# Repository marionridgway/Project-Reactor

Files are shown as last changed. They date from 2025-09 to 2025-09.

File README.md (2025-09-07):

# Project-Reactor
Smart 3D Printed UV Flow Reactor Monitoring and Control System. A digitally-controlled reactor using Arduino Uno R4 WiFi, Node-RED Dashboard, and Python for real-time monitoring, sensor logging (temperature, turbidity, UV, RGB), and  actuator control. Includes data logging to SQLite and serial integration with a customisable dashboard.

# Project Objectives

- Real-time visualisation of temperature, UV intensity, turbidity, and RGB sensor data
- Digital control of UV LEDs and peristaltic pumps
- Track and analyse dye degradation behavior
- Store all experimental data for post-run analysis using SQLite
- Sense and response of reactor parameters

# System Architecture

- Arduino UNO R4 WiFi
↓ Serial USB
- Node-Red Dashboard
↓ TCP socket (localhost)
- Python Script -> SQLite Database

# Technologies Used

- Arduino Uno R4 WiFi — Microcontroller with built-in ESP32 co-processor
- Node-RED — Dashboard and serial communication
- Python 3 — Data logger and tools
- SQLite — Local file-based database for experimental data
- Temperature Sensor: LM35 
- UV Sensor: GUVA-S12SD
- Turbidity: SKU SEN0189 
- Colour: TCS3200 
- Phototransistor: SFH 3310 
- LEDs: Blue: HLMP-AB64-TW0xx 
- LEDs UV: VAOL-5GUV8T4 
- Pumps: SKU DFR0523 

reactor-project/
├── arduino_firmware/ # Arduino .ino files and libraries
├── python_logging/ # Python scripts for logging to SQLite
├── node_red/ # Exported Node-RED flows (.json)
├── database/ # Python to SQLite .db file
├── media/ # Screenshots, wiring diagrams
└── README.md # This file

# How to Run

----> 1. Upload Arduino Firmware
- Open `arduino_firmware/` in the Arduino IDE
- Select board: `Arduino Uno R4 WiFi`
- Upload the sketch to your board

----> 2. Start Node-RED
- Control using dashboard at localhost

----> 3. Run Python Logger
- Saves data to SQLite

----> 4. Open Database (optional)
- Observe Data

# Authors

Marion Ridgway
MSc Researcher

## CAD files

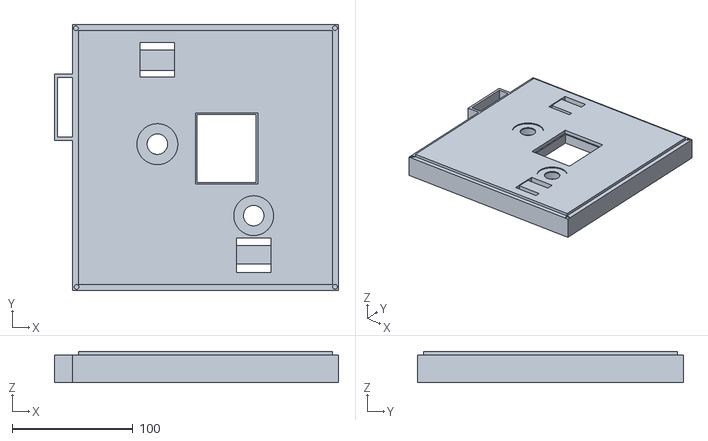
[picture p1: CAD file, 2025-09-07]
Plate_B_Sense.stl
235.0 x 220.0 x 26.0

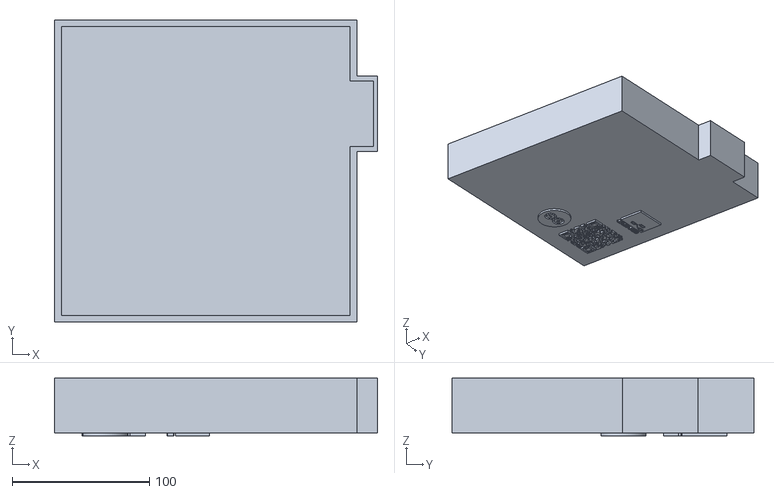
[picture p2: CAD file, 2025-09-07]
Plate_A_Top.stl
235.0 x 220.0 x 42.0

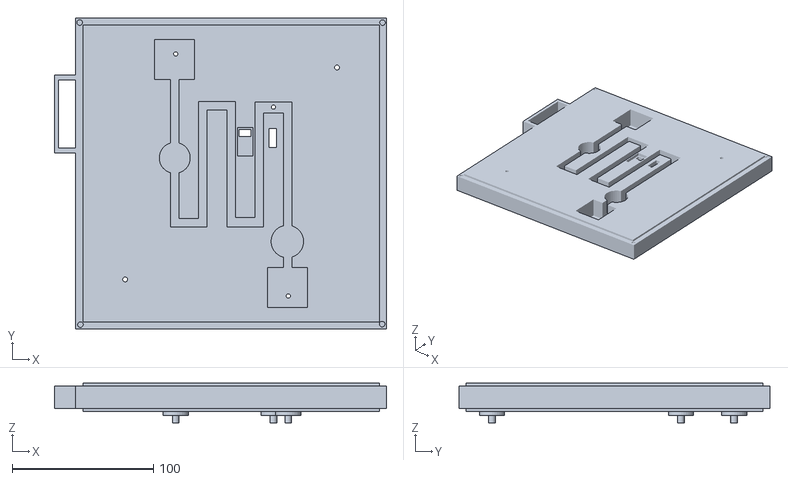
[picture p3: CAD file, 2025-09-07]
Plate_C_Flow.stl
235.0 x 220.0 x 28.0

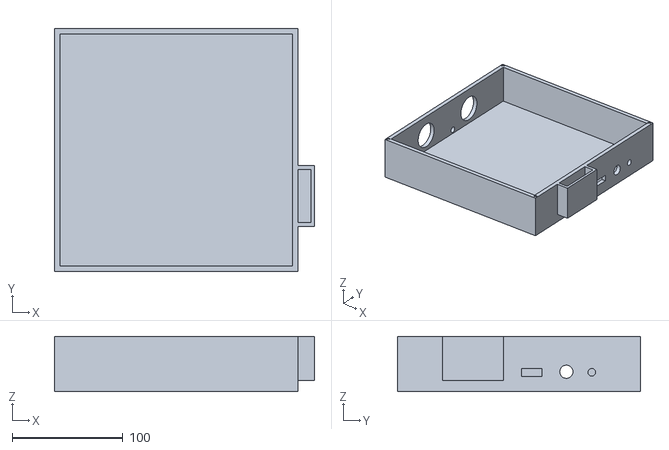
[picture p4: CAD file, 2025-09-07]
Plate_D_Base.stl
235.0 x 220.0 x 50.0

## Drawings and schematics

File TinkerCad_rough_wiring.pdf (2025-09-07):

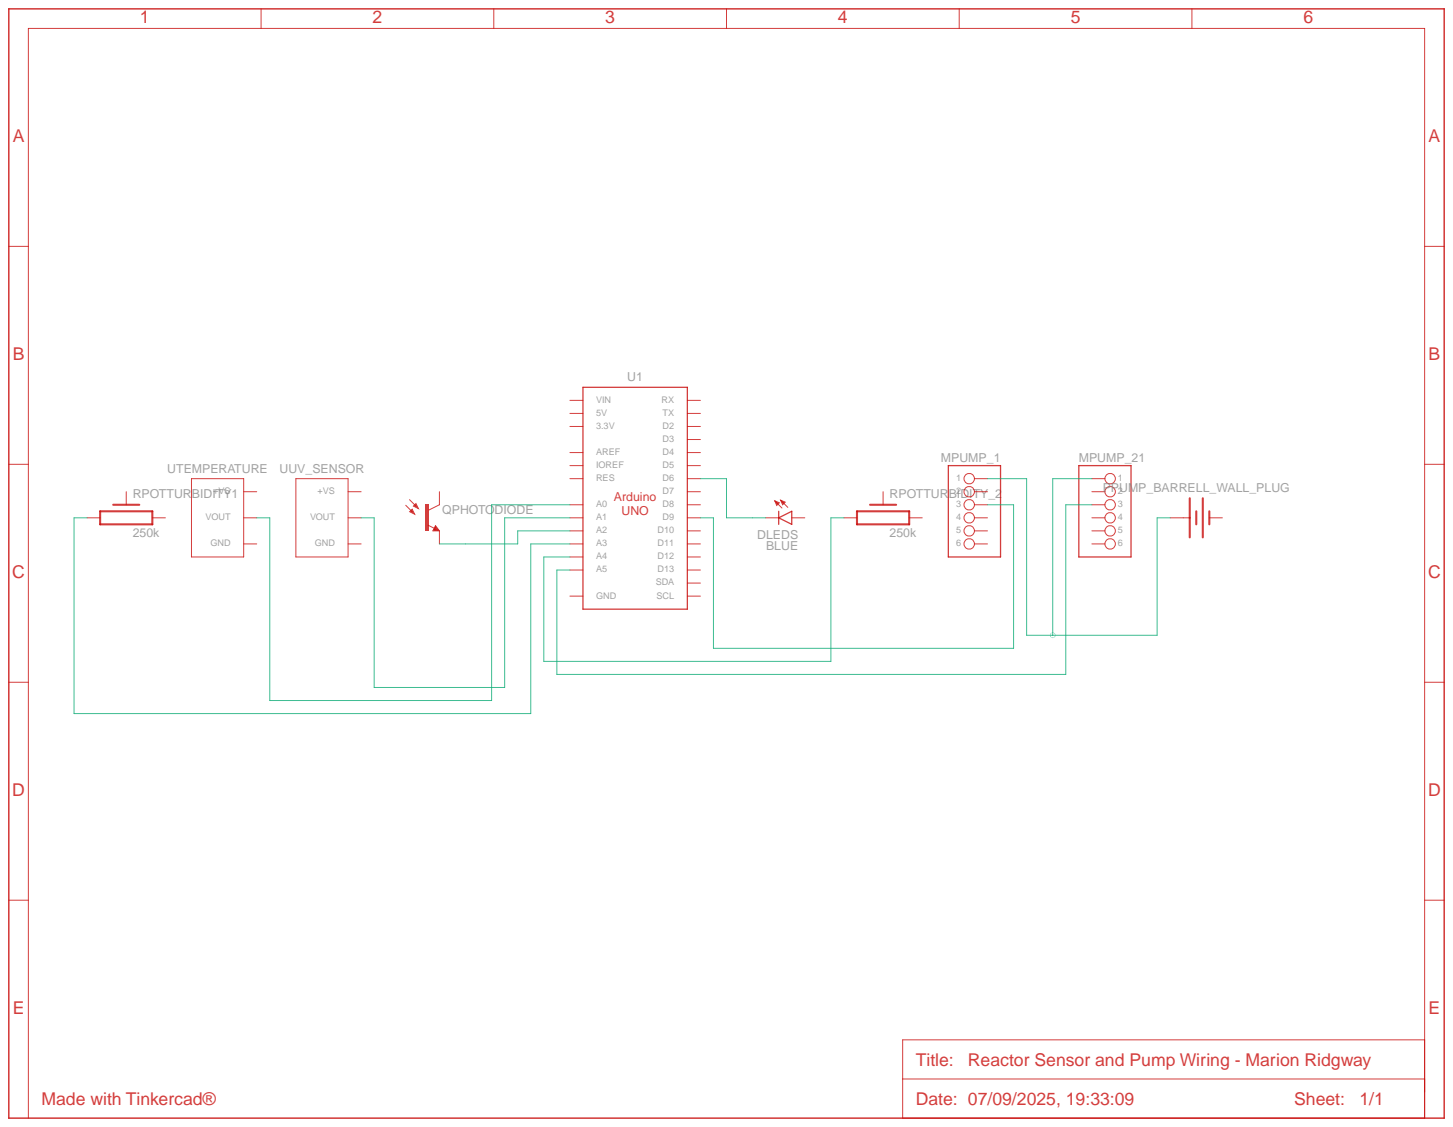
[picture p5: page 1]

Title: Reactor Sensor and Pump Wiring - Marion Ridgway

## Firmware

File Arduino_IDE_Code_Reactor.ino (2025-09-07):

/*
  Reactor Sensor Hub (Arduino)
  ---------------------------
  - Reads two TCS3200 color sensors (RGB1, RGB2)
  - RGB1 uses a fixed "Preset 1" mapping that matched wiring:
      RED=HL, GREEN=HH, BLUE=LH, CLEAR=LL  (S2/S3)
  - Reads temperature (A0), UV sensor (A1), photodiode (A2), turbidity2 (A4)
    (turbidity1 was removed; JSON keeps the key with 0.00 to avoid breaking Node-RED)
  - Drives Pump 1 (DC via GravityPump on D9) and Pump 2 (servo on A5)
  - Streams a single JSON object per loop for Node-RED

  Serial commands
  ---------------
  - "led on at intensity:<0..255>"   e.g. "led on at intensity:128"
  - "led off"
  - "pump:<mL>"                      e.g. "pump: 1.5"
  - "pump:<mL> at speed:<0..89>"     e.g. "pump: 1.5 at speed:30"
  - "pump2:<mL>"                     e.g. "pump2: 0.250"
  - "pump stop" / "pump2 stop"

  Notes
  -----
  - Keep white illumination on the sample for meaningful color readings.
  - A3 must be interrupt-capable on board for RGB1 OUT. 
*/

#include <Servo.h>
#include "GravityPump.h"
#include <EEPROM.h>
#include <math.h>

enum TCSChan { TCS_RED, TCS_GREEN, TCS_BLUE, TCS_CLEAR };

const int tempSensorPin = A0;
const int uvSensor1Pin  = A1;
const int photodiodePin = A2;
const int turbidityPin2 = A4;

const int uvLedPin1 = 6;
const int pumpPin   = 9;
const int pump2Pin  = A5;

const int s0_1 = 4, s1_1 = 5, s2_1 = 3, s3_1 = 7;
const int out_1 = A3;
const int s0_2 = 8, s1_2 = 10, s2_2 = 11, s3_2 = 12;
const int out_2 = 2;

const float alpha = 0.3f;
const unsigned GATE_MS = 100;
float vcc = 4.63;

const float pump2FlowRate   = 0.01f;
const int   pump2SpeedAngle = 10;

Servo pump2Servo;
GravityPump pump;

bool uvState = false;
bool pumpState = false;
bool pump2State = false;
int  uvLedIntensity = 0;

unsigned long pumpEndTime  = 0;
unsigned long pump2EndTime = 0;
int lastPumpSpeed = 0;

static String lastPump1Command = "";

volatile uint32_t counter1 = 0, counter2 = 0;
float r1=0,g1=0,b1=0,c1=0;
float r2=0,g2=0,b2=0,c2=0;

static inline uint8_t gamma22(float v) {
  if (v < 0) v = 0;
  if (v > 1) v = 1;
  return (uint8_t)(255.0 * pow(v, 1.0/2.2));
}

int readSmoothedAnalog(int pin, int samples = 20) {
  analogRead(pin);
  delayMicroseconds(200);
  long total = 0;
  for (int i = 0; i < samples; i++) { total += analogRead(pin); delay(2); }
  return total / samples;
}

float getCalibratedFlowRate() {
  float value;
  byte *ptr = (byte*)&value;
  for (int i = 0; i < (int)sizeof(value); i++) ptr[i] = EEPROM.read(0x24 + i);
  return value;
}

void ISR_sensor1() { counter1++; }
void ISR_sensor2() { counter2++; }

void tcsSelect(int s2, int s3, TCSChan c) {
  switch (c) {
    case TCS_RED:   digitalWrite(s2, LOW);  digitalWrite(s3, LOW);  break;
    case TCS_GREEN: digitalWrite(s2, HIGH); digitalWrite(s3, HIGH); break;
    case TCS_BLUE:  digitalWrite(s2, LOW);  digitalWrite(s3, HIGH); break;
    case TCS_CLEAR: digitalWrite(s2, HIGH); digitalWrite(s3, LOW);  break;
  }
}

uint32_t tcsReadCounts(volatile uint32_t &ctr, unsigned gate_ms) {
  noInterrupts(); ctr = 0; interrupts();
  uint32_t t0 = millis();
  while (millis() - t0 < gate_ms) {}
  noInterrupts(); uint32_t counts = ctr; interrupts();
  return counts;
}

void readTCS3200(int s2, int s3, volatile uint32_t &ctr, float &R, float &G, float &B, float &C) {
  uint32_t rC, gC, bC, cC;
  tcsSelect(s2, s3, TCS_RED);   rC = tcsReadCounts(ctr, GATE_MS);
  tcsSelect(s2, s3, TCS_GREEN); gC = tcsReadCounts(ctr, GATE_MS);
  tcsSelect(s2, s3, TCS_BLUE);  bC = tcsReadCounts(ctr, GATE_MS);
  tcsSelect(s2, s3, TCS_CLEAR); cC = tcsReadCounts(ctr, GATE_MS);
  R = alpha * (float)rC + (1 - alpha) * R;
  G = alpha * (float)gC + (1 - alpha) * G;
  B = alpha * (float)bC + (1 - alpha) * B;
  C = alpha * (float)cC + (1 - alpha) * C;
}

void readTCS3200_rgb1_fixed(int s2, int s3, volatile uint32_t &ctr, float &R, float &G, float &B, float &C) {
  uint32_t rC, gC, bC, cC;
  digitalWrite(s2, HIGH); digitalWrite(s3, LOW);   rC = tcsReadCounts(ctr, GATE_MS);
  digitalWrite(s2, HIGH); digitalWrite(s3, HIGH);  gC = tcsReadCounts(ctr, GATE_MS);
  digitalWrite(s2, LOW);  digitalWrite(s3, HIGH);  bC = tcsReadCounts(ctr, GATE_MS);
  digitalWrite(s2, LOW);  digitalWrite(s3, LOW);   cC = tcsReadCounts(ctr, GATE_MS);
  R = alpha * (float)rC + (1 - alpha) * R;
  G = alpha * (float)gC + (1 - alpha) * G;
  B = alpha * (float)bC + (1 - alpha) * B;
  C = alpha * (float)cC + (1 - alpha) * C;
}

void setup() {
  Serial.begin(9600);

  pinMode(tempSensorPin, INPUT);
  pinMode(uvSensor1Pin, INPUT);
  pinMode(photodiodePin, INPUT);
  pinMode(turbidityPin2, INPUT);
  pinMode(uvLedPin1, OUTPUT);

  pinMode(s0_1, OUTPUT); pinMode(s1_1, OUTPUT); pinMode(s2_1, OUTPUT); pinMode(s3_1, OUTPUT);
  pinMode(out_1, INPUT);
  pinMode(s0_2, OUTPUT); pinMode(s1_2, OUTPUT); pinMode(s2_2, OUTPUT); pinMode(s3_2, OUTPUT);
  pinMode(out_2, INPUT);

  digitalWrite(s0_1, HIGH); digitalWrite(s1_1, LOW);
  digitalWrite(s0_2, HIGH); digitalWrite(s1_2, LOW);

  attachInterrupt(digitalPinToInterrupt(out_1), ISR_sensor1, FALLING);
  attachInterrupt(digitalPinToInterrupt(out_2), ISR_sensor2, FALLING);

  pump.setPin(pumpPin);
  pump.getFlowRateAndSpeed();
}

void loop() {
  readTCS3200_rgb1_fixed(s2_1, s3_1, counter1, r1, g1, b1, c1);
  readTCS3200(s2_2, s3_2, counter2, r2, g2, b2, c2);

  pump.update();
  if (pumpState && millis() > pumpEndTime) pumpState = false;
  if (pump2State && millis() > pump2EndTime) {
    pump2Servo.write(90); pump2Servo.detach(); pump2State = false;
  }

  if (Serial.available()) {
    String command = Serial.readStringUntil('\n');
    command.trim();

    if (command.startsWith("led on at intensity:")) {
      int value = command.substring(command.indexOf(':') + 1).toInt();
      if (value >= 0 && value <= 255) {
        uvState = true;
        uvLedIntensity = value;
        Serial.print("UV LED ON at intensity = "); Serial.println(uvLedIntensity);
      } else {
        Serial.println("Invalid intensity value (0–255)");
      }

    } else if (command.equalsIgnoreCase("led off")) {
      uvState = false;
      Serial.println("UV LED OFF");

    } else if (command.startsWith("pump:")) {
      if (command != lastPump1Command) {
        lastPump1Command = command;
        float ml = 0; int speed = -1; bool valid = false;
        int atIndex = command.indexOf("at");
        if (atIndex > 0) {
          String volStr = command.substring(5, atIndex); volStr.trim();
          ml = volStr.toFloat();
          int speedIndex = command.indexOf("speed:", atIndex);
          if (speedIndex > -1) { speed = command.substring(speedIndex + 6).toInt(); if (speed >= 0 && speed < 90) valid = true; }
        } else { ml = command.substring(5).toFloat(); valid = true; }

        if (valid && ml > 0) {
          lastPumpSpeed = speed;
          Serial.print("Pump1 dosing "); Serial.print(ml, 2); Serial.print(" mL at "); Serial.println(speed);
          pumpState = true; pump.pumpDriver(speed, 10);
          float dur = pump.flowPump(ml); if (dur > 0) pumpEndTime = millis() + dur;
        }
      } else Serial.println("Duplicate pump command ignored");

    } else if (command.startsWith("pump2:")) {
      float ml = command.substring(6).toFloat();
      if (ml > 0) {
        unsigned long duration2 = (ml / pump2FlowRate) * 1000UL;
        Serial.print("Pump2 dosing "); Serial.print(ml, 3); Serial.println(" mL");
        pump2Servo.attach(pump2Pin);
        pump2Servo.write(pump2SpeedAngle);
        pump2State = true; pump2EndTime = millis() + duration2;
      }

    } else if (command.equalsIgnoreCase("pump stop")) {
      pumpState = false; pumpEndTime = 0; analogWrite(pumpPin, 0); Serial.println("Pump1 STOP");
    } else if (command.equalsIgnoreCase("pump2 stop")) {
      pump2Servo.write(90); pump2Servo.detach(); pump2State = false; pump2EndTime = 0; Serial.println("Pump2 STOP");
    }
  }

  analogWrite(uvLedPin1, uvState ? uvLedIntensity : 0);

  int tempRaw = readSmoothedAnalog(tempSensorPin);
  float temperature = (tempRaw / 1023.0f) * 3.3f * 100.0f;
  int uvRaw1 = readSmoothedAnalog(uvSensor1Pin);
  float uvIndex1 = (uvRaw1 * (vcc / 1023.0f)) / 0.1118f;
  int diodeRaw = readSmoothedAnalog(photodiodePin);
  float photoVoltage = diodeRaw * (vcc / 1023.0f);
  int turbidityRaw2 = readSmoothedAnalog(turbidityPin2, 20);
  float turbidityVoltage2 = turbidityRaw2 * (vcc / 1023.0f);

  float sum1 = r1 + g1 + b1;
  uint8_t R1s = gamma22(sum1 > 0 ? (r1 / sum1) : 0);
  uint8_t G1s = gamma22(sum1 > 0 ? (g1 / sum1) : 0);
  uint8_t B1s = gamma22(sum1 > 0 ? (b1 / sum1) : 0);
  float sum2 = r2 + g2 + b2;
  uint8_t R2s = gamma22(sum2 > 0 ? (r2 / sum2) : 0);
  uint8_t G2s = gamma22(sum2 > 0 ? (g2 / sum2) : 0);
  uint8_t B2s = gamma22(sum2 > 0 ? (b2 / sum2) : 0);

  Serial.print("{");
  Serial.print("\"temp\":");        Serial.print(temperature, 1); Serial.print(",");
  Serial.print("\"uvLed\":");       Serial.print(uvState ? 1 : 0); Serial.print(",");
  Serial.print("\"uvIntensity\":"); Serial.print(uvLedIntensity);  Serial.print(",");
  Serial.print("\"pump\":");        Serial.print(pumpState ? 1 : 0); Serial.print(",");
  Serial.print("\"pump2\":");       Serial.print(pump2State ? 1 : 0); Serial.print(",");
  Serial.print("\"pumpSpeed\":");   Serial.print(pumpState ? lastPumpSpeed : 0); Serial.print(",");
  Serial.print("\"flowRate\":");    Serial.print(pumpState ? getCalibratedFlowRate() : 0.0, 4); Serial.print(",");
  Serial.print("\"uv1\":");         Serial.print(uvIndex1, 1);     Serial.print(",");
  Serial.print("\"photodiode\":");  Serial.print(photoVoltage, 2); Serial.print(",");
  Serial.print("\"turbidity\":");   Serial.print(0.00, 2);         Serial.print(",");
  Serial.print("\"turbidity2\":");  Serial.print(turbidityVoltage2, 2); Serial.print(",");
  Serial.print("\"rgb1_r\":"); Serial.print((int)R1s); Serial.print(",");
  Serial.print("\"rgb1_g\":"); Serial.print((int)G1s); Serial.print(",");
  Serial.print("\"rgb1_b\":"); Serial.print((int)B1s); Serial.print(",");
  Serial.print("\"rgb2_r\":"); Serial.print((int)R2s); Serial.print(",");
  Serial.print("\"rgb2_g\":"); Serial.print((int)G2s); Serial.print(",");
  Serial.print("\"rgb2_b\":"); Serial.print((int)B2s); Serial.print(",");
  Serial.print("\"rgb1_r_raw\":"); Serial.print((int)r1); Serial.print(",");
  Serial.print("\"rgb1_g_raw\":"); Serial.print((int)g1); Serial.print(",");
  Serial.print("\"rgb1_b_raw\":"); Serial.print((int)b1); Serial.print(",");
  Serial.print("\"rgb1_c_raw\":"); Serial.print((int)c1); Serial.print(",");
  Serial.print("\"rgb2_r_raw\":"); Serial.print((int)r2); Serial.print(",");
  Serial.print("\"rgb2_g_raw\":"); Serial.print((int)g2); Serial.print(",");
  Serial.print("\"rgb2_b_raw\":"); Serial.print((int)b2); Serial.print(",");
  Serial.print("\"rgb2_c_raw\":"); Serial.print((int)c2);
  Serial.println("}");

  delay(50);
}

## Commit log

2025-09-07 Rename top top of reactor v6.stl to Plate_A_Top.stl
    [Plate_A_Top.stl]
2025-09-07 Rename Light plate and sesnors holders! v3.stl to Plate_B_Sense.stl
    [Plate_B_Sense.stl]
2025-09-07 Rename Make channel SKinner.stl to Plate_C_Flow.stl
    [Plate_C_Flow.stl]
2025-09-07 Rename reactor base with pump holes x 2 v4.stl to Plate_D_Base.stl
    [Plate_D_Base.stl]
2025-09-07 Rename Reactor Sensor and Pump Wiring - Marion Ridgway (1).pdf to TinkerCad_rough_wiring.pdf
